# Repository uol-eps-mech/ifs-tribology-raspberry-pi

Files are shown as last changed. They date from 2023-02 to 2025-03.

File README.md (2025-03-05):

# IFS Tribology Lab Raspberry Pi Data Logger

Information about setting up and using Raspberry Pi Data Loggers in the Tribology lab.

## Overview

The data logger can be used with the following machines.

* Pendulum Tribometer.
* 4 Ball Machine.
* (Others coming soon).

Each data logger contains a Raspberry Pi 4B with the following connectors:

* 2 x BNC connectors for +/-10V voltage inputs.  These are connected to either a MCC-118 (12 bit) or a MCC-118 (16 bit) data acquisition (DAQ) hat.
* 2 x K type thermocouple inputs.  These are connected to a MCC-134 thermocouple data acquisition (DAQ) hat.

In addition, the data logger used for the pendulum tribometer has a 9 way D-Sub connector that is connected to the rotary encoder.

Data sheets for the DAQ hats and for the rotary encoder can be found in the docs directory of this repo.

## Using the data loggers

__IMPORTANT__ To prevent hackers mis-using the Raspberry Pi, __the data loggers are not
connected to the internet__.

This means that the date and time are nearly always wrong as the Raspberry Pi normally updates the date and time from the internet.

At the beginning of each test run, it is a good idea to record the time shown on the data logger in your log book or similar so that you know when each test run was done and what time the data logger was showing.

You will also need to get the data off the data logger manually.  To do this, you need to plugin a USB memory stick (please use your own) and copy the files using the file manager or command line on to the memory stick.

### Thermocouple software

The MCC DAQ hats software has a nice data logger utility for the thermocouple hat.  To run it:

```bash
cd ~/daqhats/examples/c/mcc134/data_logger/logger/
./logger
```

A nice looking program starts up.

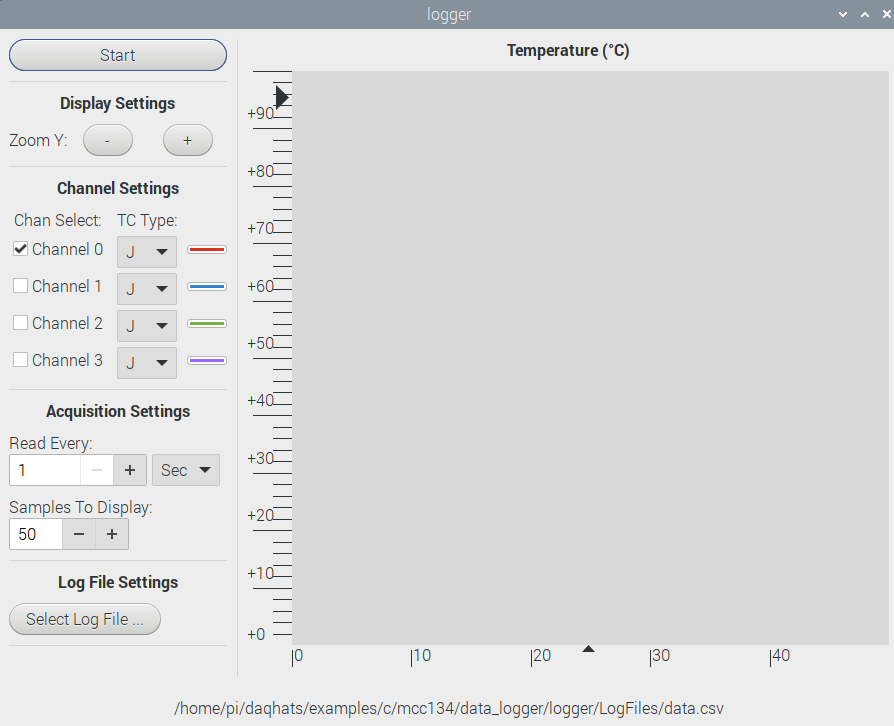
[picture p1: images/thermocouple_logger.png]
Data logger for thermocouple


Channels 0 and 1 are connected to the 2 green thermocouple connectors on the data logger box.

* Select the channel that you want to use.
* Set the `TC Type` to `K`.
* Adjust the `Acquisition Settings` as required.
* Select the log file to write to.  The name of the default file is shown at the bottom of the app, `.../dada.csv`.
* When you are ready to start recording, press `Start`.  The most recent data will be shown on the graph on the app and all the data will be written to the chosen `.csv` file.
* Press the `Stop` button when done (the start button changes to a stop button).

### Pendulum Tribometer software

The Pendulum Tribometer software records the following information:

* The speed of the test rotor in RPM.
* The voltage sent from the charge amplifier.
* The angle of the test arm from 0, calculated from the input voltage.
* The coefficient of friction, calculated from the angle.

These data are output into a CSV file for later analysis. To run the software, type the following commands in a terminal window.

```bash
cd ~/ifs-tribology-raspberry-pi/code
./start.bash
```

These commands will start two programs.  The first program is `logger.py`
that logs data from the pendulum tribometer to a CSV file.  The second
program is a graph plotting program `plotter.py`.  This program is only
intended to allow you to see roughly what is going on and
__THE GRAPHS ARE NOT STORED__.

The default name of the CSV file is "data.csv" but you can change
this as follows:

```bash
 ./start.bash my_file_name.csv
```

In this example, the data will be written to the file `my_file_name.csv`.

If you use the same data file name more than once, the previous
data file will be deleted and a new file will be written to.

To plot a graph of the data, you need to copy the CSV files that the logger
program creates onto a USB memory stick and then use Excel or similar
to create the plots that you need.

## Maintainer notes

There are some notes and photos on how the hardware is put together [here](construction/construction.md).

There are some notes on testing the final boxes [here](testing.md).

I also wrote some [design notes](design.md) for the software.

## License

This work is licensed under the MIT licence.  See LICENSE file for details.

© 2023-2025, University of Leeds.

The author, A. Blight, has asserted his moral rights.

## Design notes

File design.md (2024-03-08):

# Design notes

The software for this project is formed of three main parts:

1. The MCC DAQ examples.  These just work and do a fair bit of what we need.
2. Initial code started by Jack Rudd with a little polishing by me.
3. The final version of code.

All of the code can be found in the `code` directory.  The first versions of the code (in the `intern` directory ) were developed to get the system working and are a little rough around the edges.  They did the job but had the problem that the data was written to disk in 4k blocks.  If the program was stopped before that, the data would be lost.  This caused by the abrupt exit of the program that prevented us from calling a function to flush the buffer to disk.

After many hours of research and a lot of testing, I found [this answer on StackOverflow](https://stackoverflow.com/questions/72697369/real-time-data-plotting-from-a-high-throughput-source).  This does the classic separation of concerns thing by splitting the problem into two parts:

1. Data acquisition and recording.
2. Presentation of the data.

Some programs I developed during this testing are in the `code/trial` directory.  After some more attempts at doing this on a single file that failed, I implemented two programs started by a Bash script.  The results can be found in the `code` directory.

## Pendulum Tribometer Motor characteristics

The motor has a maximum speed of 1800RPM and a minimum speed of about 70RPM.  This means that if the last interrupt occurred more than 1 second ago, the motor is off so the speed is 0RPM.

The pendulum tribometer test rotor are connected to the motor shaft using a toothed belt.  The gear wheel on the motor shaft has 25 teeth and the gear wheel connect to the test rotor has 47 teeth.  The effective gear ration is: 25:47 or 1.88:1.

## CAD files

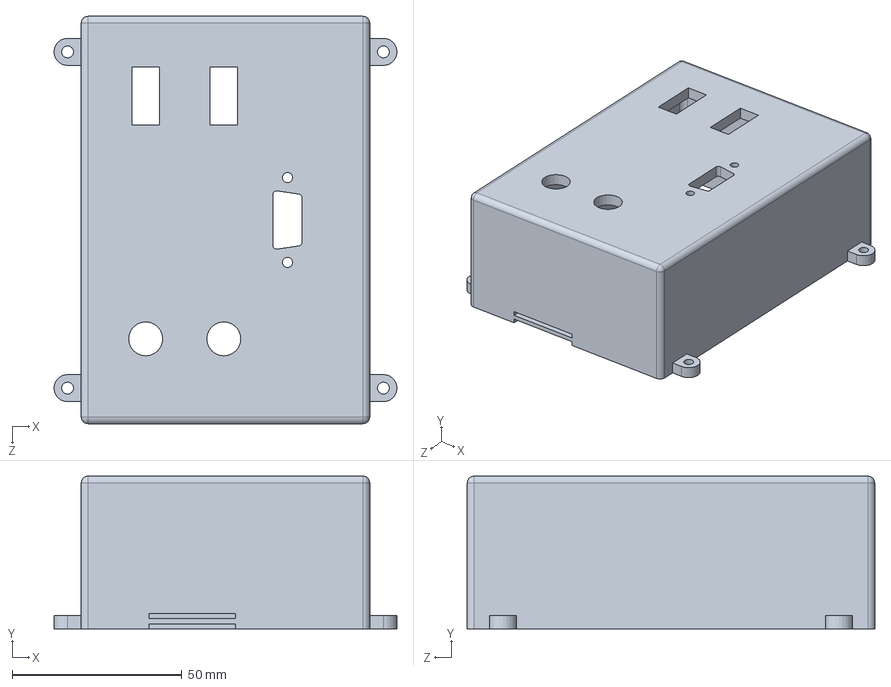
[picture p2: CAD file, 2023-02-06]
parts/pi_assem_shell_v4.SLDPRT
101.0 x 45.0 x 120.0 mm

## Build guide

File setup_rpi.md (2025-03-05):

# Raspberry Pi Set Up

How to setup the Raspberry Pi 4.

## Use the pre-built image

This is by far the quickest way.  The current image has all (except Eduroam) of the below ready to go an install in about 5 minutes.  Andy Blight knows where the images are (on his PC and backed up on the IT provided Globus file store).  The current image is `tribology_rpi_20250305.img.gz`.  The image file can be installed as follows.

### Pre-requisites

1. IMPORTANT. You need a PC that is not locked down by IT as you need Admin privileges to write to an SD card.  I use a laptop running Kubuntu.
2. The image file and copy somewhere on your PC that you can find easily.  The latest image file can be obtained from Andy Blight.
3. The Raspberry Imager software installed and ready to use.  Get it from: <https://www.raspberrypi.com/software/>
4. A micro SD card to install the OS on. The cards we use are SanDisk Extreme A2 64 GB.  The fast speeds are important when running on a Raspberry Pi.

### Installation

These instructions were run on Kubuntu 24.04LTS but should work on a Windows PC (if you have admin access).

1. Insert the micro SD card into you PC.  You may need an SD to micro SD card adapter.
2. Open the Raspberry Pi Imager program.
3. Click on the `Operating System` button.
4. Scroll to the bottom of the list and click on `Use custom`.
5. Navigate to the place you stored the image file, select it and press `Open`.
6. Press the `Storage` button.
7. Click on the SD card to use.
8. Press the `Write` button.
9. Press `Yes` when the next dialog box comes up.
10. Enter your PC password when prompted.
11. The imager program will then write the image to the card, verify the image.  This takes a few minutes.
12. When complete, a dialog pops up to tell you to remove the SD card, so do it and you're done!

## Download and install the OS

This is the hard way!

The version we are using is the Raspberry Pi OS, Debian Bullseye (32 bit) release installed using the instructions here: <https://www.raspberrypi.com/software/>. To summarise:

1. Install the Raspberry Pi Imager tool.
2. Insert SD Card.  I used this [SD card](https://www.amazon.co.uk/SanDisk-microSDHC-Adapter-Performance-SDSQUA4-032G-GN6MA/dp/B08GY9NYRM/).  Gold ones like [this](https://www.amazon.co.uk/SanDisk-Extreme-microSDHC-Adapter-Performance/dp/B06XWMQ81P/) are better!
3. On the imager tool, select
   1. The full desktop image.
   2. The SD card.
   3. Then press `Write` and wait a while (took about 20 minutes or so).  The imager downloads the image, writes it to the SD card and then verifies the image.
4. When done, eject the SD card.

## Set up the new OS

Insert the SD card into the Raspberry Pi, make sure a keyboard, mouse and and HDMI monitor is connected, then apply power.  After a while, you will get a nice picture of a sunset and a little dialog box that tells you to set up a a few things.  This is what I did:

1. Press `Next`.
2. Set Country.  The default options are for the UK so I left them alone. Press `Next`.
3. Enter a new user name (pi) and password, then press `Next`.
4. Set the screen black bars option as appropriate. Press `Next`.
5. Connect to Wi-Fi.  If you are at the University and connecting to Eduroam, press `Skip`.  Otherwise, select the Wi-Fi and press `Next`.  Then enter the Wi-Fi password and press `Next`.
6. Update Software.  Press `Skip` if no Wi-Fi, or `Next` to update.  The software update will take an hour or so, so I prefer to skip this step and do the update later.
7. Press `Restart`.

After restarting, we need to start customising our Pi.

1. Add a few useful tools.
   1. Connect to the network.  Eduroam can be used if you know how but it is quicker and easier to hotspot to your phone (assuming you have a good data allowance).
   2. Execute these commands:

       ```bash
       cd
       git clone https://github.com/andyblight/bash_scripts.git
       ```

       A new directory will be created called `bash_scripts`.
   3. Now run the following commands:

       ```bash
       cd ~/bash_scripts
       ./install.sh ubuntu22.04lts
       cd ubuntu22.04lts/desktop-installs/
       ./install-git-tools.sh
       ```

     This will install some tools that I find useful when working on Debian/Ubuntu PCs and the Raspberry Pi.  The tools are:

     * `vim` a command line text editor.
     * `gitk` a viewer for the history of a `git` repo.
     * Some custom `Bash` enhancements in `~/.bash_aliases`.
     * Some `git` aliases in `~/.gitconfig`.
     * A nice system update script.
   4. Start a new terminal shell to pick up the enhancements from the `Bash` aliases.

2. Now that most of the setup has been done, it is time to do that update that you've been putting off.  Time to run the system update script.  In a terminal windows on the RPi, run `upgrade.sh` and let it go!  A full update may take up to an hour, so be prepared to wait.

## Setup software for the MCC DAQ cards

This is fairly simple.  Clone the MCC-DAQ hats repo and build the code.

```bash
cd ~
git clone https://github.com/mccdaq/daqhats.git
cd ~/daqhats
sudo ./install.sh
sudo pip install -break-system-packages daqhats
sudo daqhats_read_eeproms
```

If you are using new DAQ hats, you may need to update the firmware on them.  Instructions for this can be found in the file `~/daqhats/README`.

__NOTE: As of 5 March 2025, thermocouple data logger app no longer builds due to problems with various libraries not being available.  Needs to be fixed at some point.__

To build the thermocouple data logger app:

```bash
sudo apt install -y libgtkdatabox-dev
cd ~/daqhats/examples/c/mcc134/data_logger/logger
make
```

This builds a new app called `logger`.  Run it and check that it start up correctly and that thermocouples return the correct values when plugged into the sockets.

## Clone this repo

Finally, clone this repo:

```bash
cd ~
git clone https://github.com/uol-eps-mech/ifs-tribology-raspberry-pi.git
```

Done! Time for a well deserved cup of tea.

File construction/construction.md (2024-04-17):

# Construction

## BOM

Per unit

* 1 x 3D printed case.  Custom design.
* 2 x BNC sockets, chassis mount. <https://uk.rs-online.com/web/p/coaxial-adapters/5464083>
* 2 x K type thermocouple sockets. <https://uk.rs-online.com/web/p/sensor-accessories/4559742>
adafruit-perma-proto-hat-for-pi-mini-kit?variant=1038451613>
* 1 x MCC 118/128 DAQ HAT - <https://uk.rs-online.com/web/p/raspberry-pi-hats-add-ons/2306179?gb=b> or <https://uk.rs-online.com/web/p/raspberry-pi-hats-add-ons/2306180?gb=b>
* 1 x MCC134 DAQ HAT <https://uk.rs-online.com/web/p/raspberry-pi-hats-add-ons/2306181>
* 4 x Case screws M3 16mm (comes in a pack 100): <https://uk.farnell.com/tr-fastenings/m3-16-krstmc-z100/screw-pozi-csk-steel-bzp-m3x16/dp/1420400>
* 4 x Fan screws M2.5 12mm (comes in a pack 100): <https://uk.farnell.com/tr-fastenings/dm2-516prstmcz100din7985/screw-pan-head-pozi-steel-m2-5/dp/2506091>

Optional (when encoder fitted)

* 1 x 9 way D-Sub female chassis mount.  <https://uk.rs-online.com/web/p/D-Sub-connectors/7873852>
* 1 x Adafruit Perma-Proto board ADA2310 - <<https://shop.pimoroni.com/products/>

Additional parts (needed but not in single unit quantities)

* 1 box of stand offs - <https://www.amazon.co.uk/GeeekPi-Standoffs-Assortment-Box%EF%BC%8CMale-Female-Screwdriver/dp/B07PHBTTGV>
* 1 pack of 2 fans and heat sinks. - <https://www.amazon.co.uk/GeeekPi-Raspberry-30x30x7mm-Brushless-Retroflag/dp/B07FVQG926/>

NOTE: The fans have M2.5 15mm screws.  These are used to screw the base of the case to the Raspberry Pi assembly.  The M2.5 12mm screws are then used to hold the fans in place.

## Wiring of rotary encoder

The rotary encoder fitted to the pendulum tribometer is made by British Encoder
Products and has the following specifications:

* model 15/T/OC
* pulse per revolution (PPR) count of 1200
* Power supply voltage: 5 to 24V

The rotary encoder outputs that we use are:

A - Rotary encoder position A - 1200 pulses per revolution.
B - Rotary encoder position B - 1200 pulses per revolution.
Z - Rotary encoder index - one pulse per revolution.

As the outputs from the encoder are open collector, 2k2 pull up resistors connected to the 3V3 rail have been added to the proto-board for each GPIO input.

A 9 way D-Sub connector is used to connect the encoder to the data logger.  The pins are allocated in the table below.

| GPIO Pin | D-Sub Pin | Encoder Colours | Encoder names |
|---|---|---|---|
| Ground | 1 | Black  | Ground |
| 5V     | 2 | White  | VCC |
| GPIO23 | 3 | Brown  | B |
| GPIO04 | 4 | Red    | A |
| GPIO22 | 5 | Orange | Z |

```text
   -------------
   \ 5 4 3 2 1 /
    \ 9 8 7 6 /
     ---------
```

The 9 way D-Sub connector pin number when viewed from outside of case.

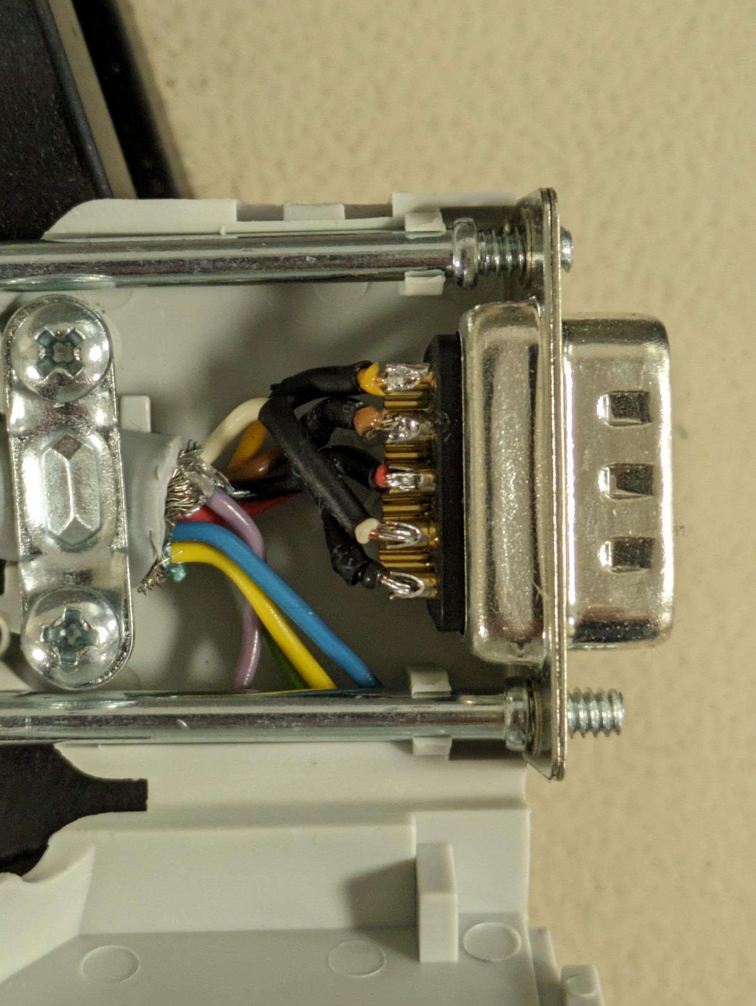
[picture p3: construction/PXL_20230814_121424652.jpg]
Photo of plug internals


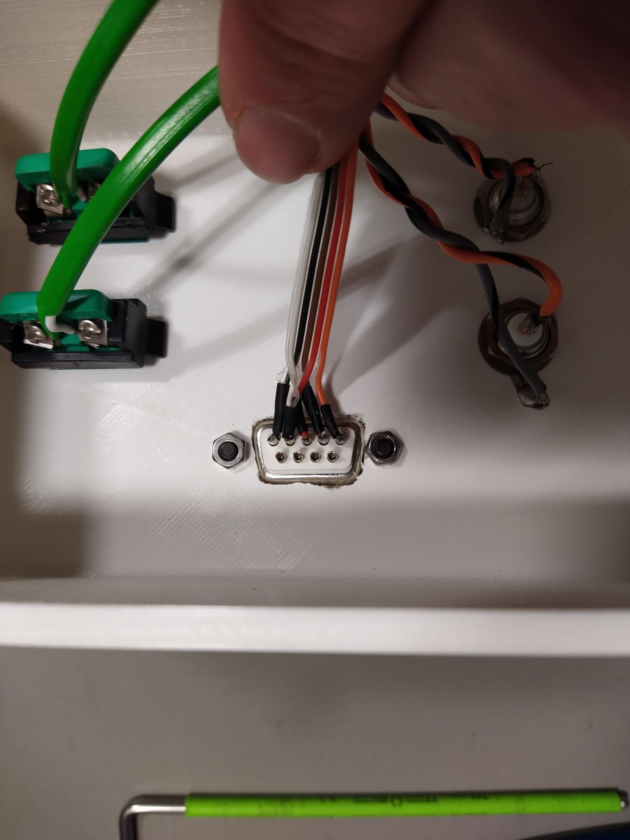
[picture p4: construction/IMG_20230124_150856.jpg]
Wiring on back of socket


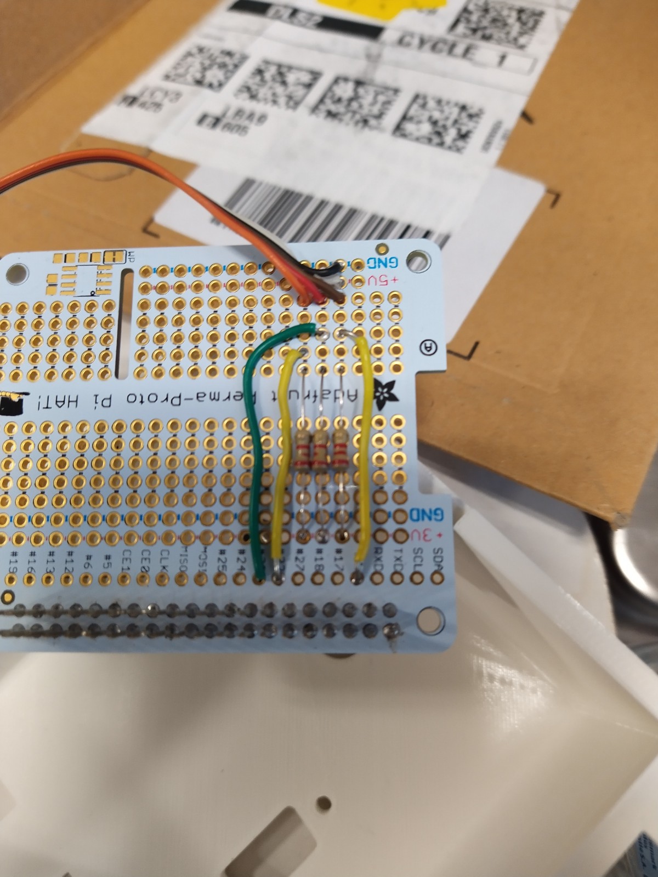
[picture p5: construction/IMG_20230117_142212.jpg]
Protoboard wiring


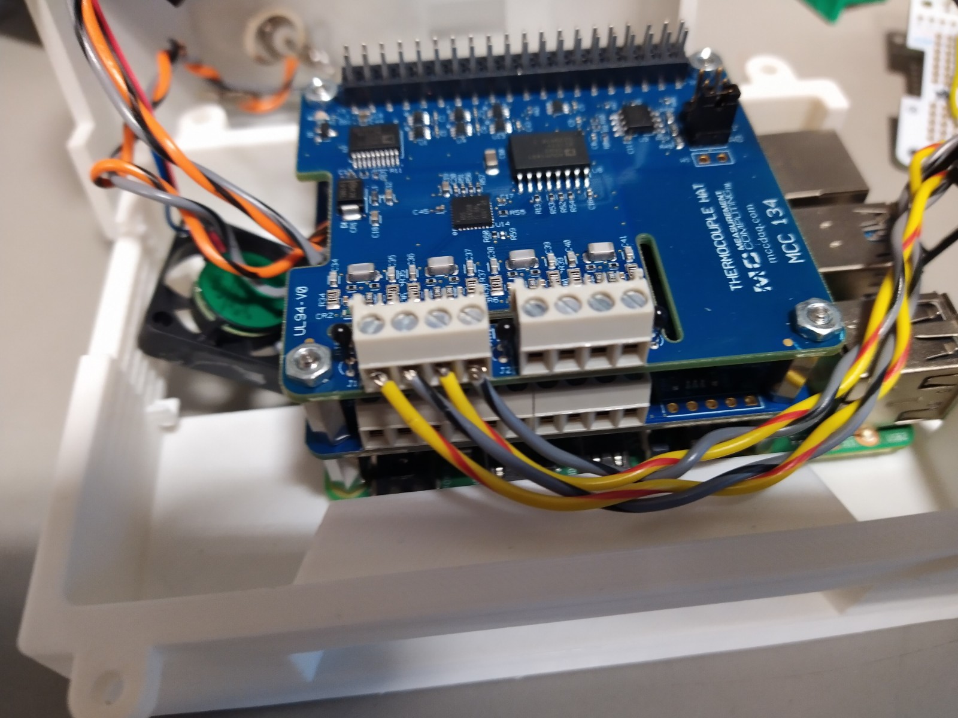
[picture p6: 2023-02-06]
construction/IMG_20230117_123502.jpg

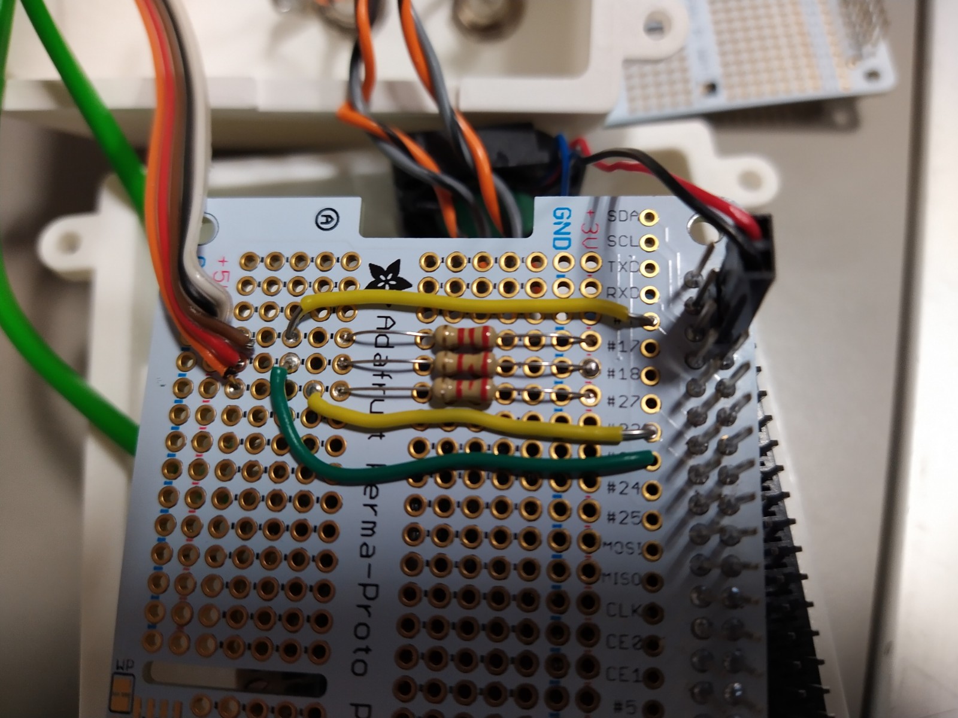
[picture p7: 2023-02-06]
construction/IMG_20230124_141944.jpg

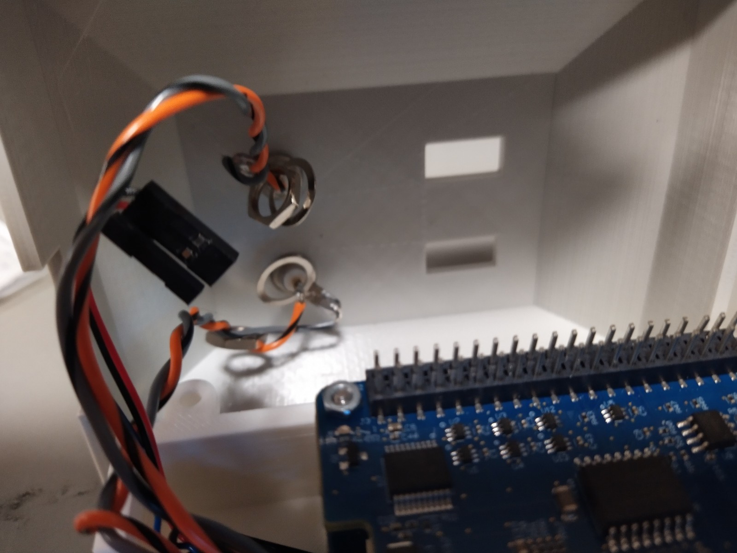
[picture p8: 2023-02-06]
construction/IMG_20230117_123519.jpg

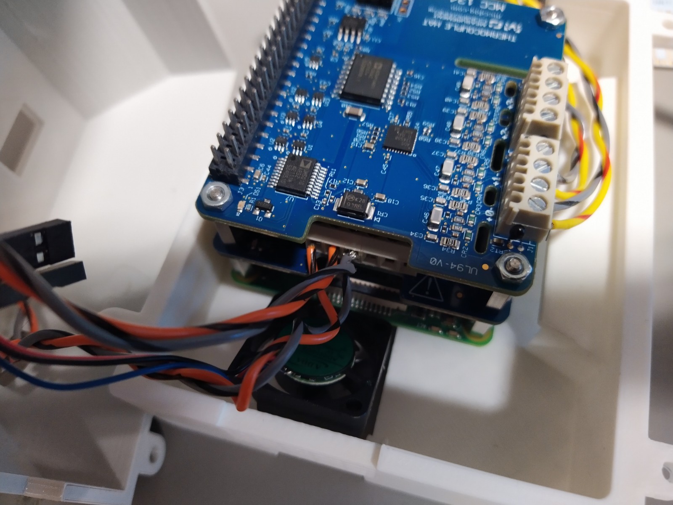
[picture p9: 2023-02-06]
construction/IMG_20230117_123509_1.jpg

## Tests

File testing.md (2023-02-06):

# Testing the boxes

Once the software for the MCC DAQ hats has been installed, you can test the connections on the top of the box as follows.

## Verify Pi boots

1. Insert an SD card with the correct image into the Raspberry Pi.
2. Connect the HDMI, power, keyboard and mouse to the Raspberry Pi.
3. Power on.  Verify that the Pi boots.  Should take less than 30 seconds.
4. Verify that the keyboard and mouse works.
5. From the start menu, select `Accessories`, then open `MCC DAQ HAT Manager`.
6. Press the `List devices` button.  A dialog box should be shown that displays the following information:
   * 2 boards have been found.
   * Address 0 board is the MCC118 or MCC128 voltage input hat.
   * Address 1 board is the MCC134 thermocouple input hat.
7. Close the `List devices` dialog.
8. Open the MCC118 or MCC128 control app.  Press the `Open` button to
9. Apply a known voltage to the top BNC connector.  Verify that the expected voltage is shown on channel 0 of the app.
10. Repeat for the other BNC connector. Verify that the expected voltage is shown on channel 1 of the app.
11. Close app.
12. Open the MCC134 control app.  Select K type for channel 0 and channel 1.
13. Plug in K type thermocouple to top thermocouple socket. Verify that the expected temperature is shown on channel 0 of the app.
14. Plug in K type thermocouple to bottom thermocouple socket. Verify that the expected temperature is shown on channel 1 of the app.
15. Close app.

## Test rotary encoder inputs

If there is a 9 way DSUB female connector fitted to the box, perform the following tests.

1. Open a LXTerminal window.
2. Run the command `raspi-gpio get 4,22,23`.
3. Verify that all pins have `level=1`.
4. Insert jumper wire from pin 1 (ground) to pin 3.
5. Run the command `raspi-gpio get 4,22,23`.
6. Verify that GPIO4 and GPIO422 have `level=1`, and GPIO23 has `level=0`.
7. Insert jumper wire from pin 1 (ground) to pin 4.
8. Run the command `raspi-gpio get 4,22,23`.
9. Verify that GPIO22 and GPIO23 have `level=1`, and GPIO4 has `level=0`.
10. Insert jumper wire from pin 1 (ground) to pin 5.
11. Run the command `raspi-gpio get 4,22,23`.
12. Verify that GPIO4 and GPIO423 have `level=1`, and GPIO22 has `level=0`.

9 way DSUB connector pin number when viewed from outside of case.

Mappings of D-SUB pins to GPIO pins.

| DSUB Pin | Usage |
|---|---|
| 1 | Ground |
| 2 | 5V |
| 3 | GPIO23 |
| 4 | GPIO04 |
| 5 | GPIO22 |

```text
   -------------
   \ 5 4 3 2 1 /
    \ 9 8 7 6 /
     ---------
```

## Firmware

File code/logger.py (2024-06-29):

#!/usr/bin/env python3

""" A program that logs data from the Pendulum Tribometer.
    Currently only supports a single channel, channel 0.
"""

import math
import os
import sys
import time
import random
from datetime import datetime
from argparse import ArgumentParser
from daqhats import hat_list, HatIDs, mcc118
import RPi.GPIO as GPIO

# The interval between each reading in seconds.
INTERVAL_S = 0.1
CSV_HEADER_STRING = "Time,RPM,Voltage,Angle Degrees,Coefficient of friction\n"

# GPIO pin for the encoder.
ENCODER_Z_GPIO = 22

# Plate on back says max speeds are:
# Fast shaft = 1800. This is what the encoder reports.
# Slow shaft speed = 417.  This is the outpu from the gearbox.
MOTOR_GEARBOX_RATIO = 417 / 1800

# 25 teeth on motor, rotor end has 47.
BELT_RATIO = 25 / 47

# Value to divide the encoder pulses by to get the rotor speed.
ROTOR_RATIO = MOTOR_GEARBOX_RATIO * BELT_RATIO

# Maximum RPM of motor is 1800rpm.
MAX_MOTOR_RPM = 1800

# Input voltage offset. The value being read it is not always zero
# when the pendulum is centred, so change this value as needed.
PENDULUM_OFFSET_VOLTAGE = 0.0

def convert_voltage_to_values(voltage_v):
    """ Converts the input voltage into an angle and then into a
    co-efficent of friction value.
    """
    # Convert reading into a tuple of values.
    corrected_voltage_v = voltage_v + PENDULUM_OFFSET_VOLTAGE
    # Calibration value taken experimentally from the pendulum.
    angle_DEG = (corrected_voltage_v) * 9.5
    angle_RAD = (angle_DEG * 3.14159265) / 180
    # Processing angle data to Friction data
    coefficient_of_friction = abs(math.sin(angle_RAD)) / (math.tan(1.0472))
    return (corrected_voltage_v, angle_DEG, coefficient_of_friction)


# class FakeMCC118DAQ:
#     """A fake version of the MCC-118 DAQ class that returns a value with some
#     random noise on it so that some changes are visible.
#     """

#     def __init__(self):
#         pass

#     def get_reading(self, channel):
#         """Return a value simulating a voltage.
#         Each channel has a different central voltage.
#         """
#         if channel == 0:
#             value = 1.0 + random.random()
#         elif channel == 1:
#             value = 2.0 + random.random()
#         # Convert reading into a tuple of values.
#         # Value taken from the difference at 0
#         voltage = value + 0.3
#         # Calibration value taken experimentally from the pendulum.
#         angle_DEG = (voltage) * 9.5
#         angle_RAD = (angle_DEG * 3.14159265) / 180
#         # Processing angle data to Friction data
#         coefficient_of_friction = abs(math.sin(angle_RAD)) / (math.tan(1.0472))
#         return (voltage, angle_DEG, coefficient_of_friction)


class MCC118DAQ:
    """Provides functions to use the MCC-118 DAQ hat."""

    def __init__(self):
        self.board = None
        self.board_list = hat_list(filter_by_id=HatIDs.ANY)
        if not self.board_list:
            print("No boards found")
            sys.exit()
        else:
            for entry in self.board_list:
                if entry.id == HatIDs.MCC_118:
                    self.board = mcc118(entry.address)
                    break

    def get_voltage(self, channel):
        """Return the voltage in Volts for the given channel."""
        voltage_v = 0.0
        if channel == 0 or channel == 1:
            voltage_v = -1.0 * self.board.a_in_read(channel)
        return voltage_v


# class FakeEncoder:
#     def __init__(self):
#         pass

#     def get(self):
#         # Fake value for now.
#         rpm = 25.0 + (random.random() * 0.5)
#         return rpm

#     def close(self):
#         pass


class Encoder:
    def __init__(self) -> None:
        self._rpm = 0.0
        self._last_datetime = datetime.now()
        GPIO.setmode(GPIO.BCM)
        # External pull up resistors are fitted.
        GPIO.setup(ENCODER_Z_GPIO, GPIO.IN)
        GPIO.add_event_detect(ENCODER_Z_GPIO, GPIO.FALLING, callback=self.interrupt_callback)

    def get_rpm(self) -> float:
        return self._rpm

    def interrupt_callback(self, channel) -> None:
        # Each interrupt happens exactly once per revolution.
        now = datetime.now()
        # print(now)
        # Calculate interval between last interrupt and this one.
        delta = now - self._last_datetime
        # Motor minimum speed is about 70RPM, so interrupts should be less then 1 second apart.
        # If the last interrupt was more than 1 second ago the motor has stopped.
        if delta.total_seconds() > 1.0:
            self._rpm = 0.0
        else:
            # Convert delta time to RPM.
            new_rpm = (1.0 / delta.total_seconds()) * 60
            # print("new_rpm {}".format(new_rpm))
            # Some values produced are completely wrong, possibly caused
            # by electrical noise.
            if new_rpm <= MAX_MOTOR_RPM:
                self._rpm = new_rpm
        # Save now for later...
        self._last_datetime = now


class Logger:
    def __init__(self):
        # Start the encoder driver.
        # self._encoder = FakeEncoder()
        self._encoder = Encoder()
        # Start the DAQ driver.
        # self._daq = FakeMCC118DAQ()
        self._daq = MCC118DAQ()
        self._running = True
        # Record start epoch time.
        self._start_time = time.time()

    def _get_formatted_output(self):
        # Get RPM.
        motor_rpm = self._encoder.get_rpm()
        rotor_rpm = motor_rpm * ROTOR_RATIO
        # Get data from channel 0.  Change to 1 if needed.
        voltage_v = self._daq.get_voltage(0)
        voltage, angle_DEG, coefficient_of_friction = convert_voltage_to_values(voltage_v)
        # Get the time since program started in seconds.
        duration = time.time() - self._start_time
        # Create formatted string.
        output_string = "{:.3f},{:.3f},{:.3f},{:.3f},{:.3f}\n".format(
            duration, rotor_rpm, voltage, angle_DEG, coefficient_of_friction
        )
        # Debug. Can comment out if annoying.
        print(output_string)
        return output_string

    def run(self, filename, interval_s):
        with open(filename, "w") as logger_file:
            # Write header.
            print(CSV_HEADER_STRING)
            logger_file.write(CSV_HEADER_STRING)
            try:
                while True:
                    output_string = self._get_formatted_output()
                    logger_file.write(output_string)
                    # Make sure the data are written immediately.
                    logger_file.flush()
                    time.sleep(interval_s)
            except KeyboardInterrupt:
                print("Stopped by user")


def get_args():
    parser = ArgumentParser()
    parser.add_argument("filename", help="write report to FILE", metavar="FILE")
    return parser.parse_args()


def main():
    args = get_args()
    logger = Logger()
    logger.run(args.filename, INTERVAL_S)
    os.sync()


if __name__ == "__main__":
    main()

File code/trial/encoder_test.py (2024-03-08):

#!/usr/bin/env python3

"""
Generate a revolutions per minute value from the rotary encoder.

An interrupt driven callback calculates the time taken between the current
interrupt and the last interrupt.  This time difference is then used to
calculate the RPM value that can be read by another process.
"""

import signal
import sys
import time
import RPi.GPIO as GPIO
from datetime import datetime
from threading import Thread

# The GPIO pin being used.  We only check the Z output (1 pulse = 1 RPM).
ENCODER_Z_GPIO = 22

# Plate on back says max speeds are:
# Fast shaft = 1800. This is what the encoder reports.
# Slow shaft speed = 417.  This is the outpu from the gearbox.
MOTOR_GEARBOX_RATIO = 417 / 1800

# 25 teeth on motor, rotor end has 47.
BELT_RATIO = 25 / 47

# Value to divide the encoder pulses by to get the rotor speed.
ROTOR_RATIO = MOTOR_GEARBOX_RATIO * BELT_RATIO


class Encoder:
    def __init__(self) -> None:
        self._rpm = 0.0
        self._last_datetime = datetime.now()
        GPIO.setmode(GPIO.BCM)
        # External pull up resistors are fitted.
        GPIO.setup(ENCODER_Z_GPIO, GPIO.IN)
        GPIO.add_event_detect(
            ENCODER_Z_GPIO, GPIO.FALLING, callback=self.interrupt_callback
        )

    def get_rpm(self) -> float:
        # Motor minimum speed is about 70RPM, so interrupts should be less then 1 second apart.
        # If the last interrupt was more than 1 second ago the motor has stopped.
        delta = datetime.now() - self._last_datetime
        rpm = self._rpm
        if delta.total_seconds() > 1.0:
            rpm = 0.0
        return rpm

    def interrupt_callback(self, channel) -> None:
        # Each interrupt happens exactly once per revolution.
        now = datetime.now()
        # print(now)
        delta = now - self._last_datetime
        # Convert to RPM.
        self._rpm = (1.0 / delta.total_seconds()) * 60
        # Save now for later...
        self._last_datetime = now


def signal_handler(sig, frame):
    GPIO.cleanup()
    sys.exit(0)


def print_loop() -> None:
    print("Loop started")
    encoder = Encoder()
    while True:
        time.sleep(1.0)
        encoder_rpm = encoder.get_rpm()
        rotor_rpm = encoder_rpm * ROTOR_RATIO
        print("Motor = {}RPM, rotor {}RPM ".format(encoder_rpm, rotor_rpm))


def main() -> None:
    print_thread = Thread(target=print_loop)
    print_thread.start()
    signal.signal(signal.SIGINT, signal_handler)
    #  The program waits until killed when pause() is called.
    signal.pause()


if __name__ == "__main__":
    print("Started")
    main()
    print("Done")

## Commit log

2023-01-27 Added testing notes.
    Also added photos of internal wiring, datasheet for rotary encoder.
2023-02-06 Added Solidworks model of top of case
    [pi_assem_shell_v4.SLDPRT]
2023-03-07 Tried to make it flush.
    Needs way to kill thread from keyboard interrupt.
2023-03-25 Output in the correct format.
    Copied conversion of the voltage value read fromthe DAQ into the angle
    and the coefficent of friction.
2023-03-27 Version ready for testing on RPi.
    The Encoder class needs to be implemented and currently returns 0 RPM.
    The MCC118 class is faked for now. The real one needs to be enabled and tested.
    Everything else works.
2023-03-28 Enabled MCC118 DAC. Works.
    Enabled MCC118 DAQ and fixed the problems that needed fixing.
    Also removed the 0.3V offset that was added. This offset can be removed by
    correctly manually setting up the Tribometer.
2024-04-17 Update construction.md
    Added extra screws needed for the new case.
